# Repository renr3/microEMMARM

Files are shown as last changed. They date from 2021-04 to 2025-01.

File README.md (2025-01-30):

# microEMMARM
This is the official repository of the microEMMARM system. 

This repository was built and will be maintaned to provide all the necessary resources to deploy the open-source microEMMARM test system and perform an EMM-ARM test with it. This repository will constantly be updated for bug fixes, new versions and other updates/fixes. **Keep an eye on it!**

The microEMMARM project is released under MIT license. If you want to use for commercial ends, please check the restrictions imposed by the licenses that bind this work (both microEMMARM and the libraries that it uses). 

Punctual static releases made available in Zenodo will also be archived here.

If you are  interested in more details, explanation and results concerning the microEMMARM system, please check the papers below. Also, if you use this repository in some way, please consider citing a research paper that reports on this work:

1. **Rocha Ribeiro, R., Russo, T., Araghi, A., Granja, J. L., Azenha, M., & Lameiras, R. (2025). Design and validation of a minimalist, open-source system for measuring elastic modulus evolution in cementitious materials. Nondestructive Testing and Evaluation, 1–25.** 
2. Rocha Ribeiro, R., Sousa, M.I.C., Rêgo, J.H.d. Lameiras, R. Innovative low-cost system for early age E-modulus monitoring of cement pastes: validation and application to nanosilica-added and limestone-calcined clay cements. Mater Struct 55, 13 (2022). https://doi.org/10.1617/s11527-021-01849-w 
3. A cost-effective micro-controller based system for EMM-ARM tests in cement paste**: Rocha Ribeiro, R.; Granja, José; Lameiras, Rodrigo; Azenha, Miguel. (2022). Synercrete'23 conference. To be published.
4. R. Ribeiro and R. Lameiras, “Monitoring of elastic modulus evolution on concrete with a low-cost test system,” 2021, doi: https://doi.org/10.6084/m9.figshare.14773329.v1. 
5. R. Rocha Ribeiro, J. H. S. Rêgo, and R. Lameiras, “Elastic modulus evolution of cement pastes since early ages: development and application of a test system,” in Anais do 62o Congresso Brasileiro do Concreto - CBC2020, 2021, pp. 1–10, [Online]. Available: https://www.researchgate.net/publication/357605792_Elastic_modulus_evolution_of_cement_pastes_since_early_ages_development_and_application_of_a_test_system.

Any doubts, questions or messages may be directed to renan.rocha.ribeiro@gmail.com

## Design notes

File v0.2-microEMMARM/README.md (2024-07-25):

# microEMMARM v0.2

This is the official repository of microEMMARM v0.2, a microcontroller-based system for performing EMM-ARM (Elastic Modulus Measurement through Ambient Response Method) tests. Previous versions can be found in the other subrepos in this same repository (_i.e._, "V0.1.b-Synercrete23" and "v..1.a-Zenodo").

The information contained here are self-sufficient for allowing full reproduction of the data-acquisition hardware necessary for performing an EMM-ARM test. It includes the data-acquisition and storage hardware and the accelerometer sensors. As an output, this system will produce a series of ".emm" files, a binary-formatted file. To post-process these files and obtain the elastic modulus evolution, check the open-source post-processing software in https://github.com/renr3/postProcess-EMMARM.

For this version v0.2, the resources available are:

1. **cases**: files to support the production of hardcases for storing the system. There are two versions available: version 1, designed primarily for manufacturing with industrial plastic but that can also be manufactured with 3D printing; version 2, designed primarily to be produced in a small 3D printer, by printing small parts of the box and assemble it later with glue.
2. **documentation**: this folder is meant to contain information relevant to understanding design and working options for the system.
3. **libraries**: the necessary Arduino libraries for the source code of the hardware system
4. **pcb**: these are all the files necessary to build the PCB (printed circuit board) of the data-acquisition system. You can find: (i) the datasheets of each of the components used in the current implementation (so you may find the exact same ones or decide on substitutions); (ii) the gerber files in case you want to order the PCB from a manufacturer like https://jlcpcb.com/; (iii) an Excel spreadsheet with the bill of materials, containing the description, quantitiy, and estimated costs and links from three online suppliers; (iv) a Fritzing file with the schematics of the system to support building over a PCB, a solderable perfboard, or a PCB; (iv) a block diagram with the parts mapping, to aid in the navigation of the project files.
5. **source**: this is the Arduino source code that you would need to upload to the microcontroller. This version was designed for the ATMega328p microcontroller, but there should be no problem in using it with similar microcontrollers.

As mentioned in the root folder, the microEMMARM project is released under the MIT license, but please check the underlying licenses on the other libraries (check **libraries** folder) to see if your intended use is somewhat restricted.

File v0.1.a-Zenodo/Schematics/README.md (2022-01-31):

These schematics were developed in the Fritzing software (https://fritzing.org/).

Gerber files generated from the Fritzing software are also included.

For first time builders, it is recommended to follow the schematics in a solderless breadboard, or on a soldered perfboard, so a better understanding of the circuit is attained. For experienced users in electronics, the Gerber files may be used to directly print a PCB board.

The microEMMARM schematics currently have the following versions:

- beta_v0.0: this is the bare-minimum version, as shown in the Figure 3 of the research paper "Low-cost system for early age E-modulus monitoring of cement-based materials". This version does not have Gerber files. It is mainly intended for implementation on a solderless breadbor or a solderable breadbord (aka perfboard) for first time implementers.
- beta_v0.1: this is the bare-minimum version with added ADC channels and digital channels for controlling external devices through a digital interface (e.g. motors for artificial excitation). This version is still under testing and will be added in the near future. This version has Gerber files for PCB printing.

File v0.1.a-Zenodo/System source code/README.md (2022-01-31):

This folder contains the Arduino source code files required by the microprocessor to perform the automated tasks. 

In order to open the file and upload to the Arduino or to a properly bootloaded microprocessor, the user shall use the latest version of the Arduino IDE.

Installation of the libraries used by the source code may be required during uploading the source code.

The source code folders are named to indicate the respective hardware version they were built upon. Make sure you use the correct one, otherwise your system may not function well or may not function at all. In the end of the folders' name, the numeric code indicates the date that version was released, so to allow various source code versions for a given hardware design.

A brief summary of each version is presented here:

- **beta_v0.0-2104**: source code for beta_v0.0 hardware. Main features: single ADC channel; user interface comprised of 3 LEDs and a buttom; ADS1115 running on continuous mode with ALRT pin.

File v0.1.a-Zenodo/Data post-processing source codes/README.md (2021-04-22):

This folder contains the source codes of the software for EMM-ARM data post-processing and E-modulus estimation.

The source codes were developed in the MATLAB programming environment. Installation of the required toolboxes may be required.

The following 3 .m files were developed, and need to be subsequently manually run to perform all the post-processing tasks required during EMM-ARM data processing. 

Further improvements will aim towards building an integrated user interface for all these codes.

# 1 - Iterative frequency identification in all files (1_freqId file)

1. The code starts by asking the user to select the folder that contains all the test files.

2. The code iterates through each of the test files.

3. In each test file, the code automatically estimates the first "n" frequencies by using the peak-picking method.

4. In the beggining of the code, some configuration variables shall be set by the user: number of frequencies to be identified, digital filtering characteristics, etc.

5. The code generates a text file in which the time and frequency of each test file is printed in a space-separated file

# 2 - Iterative E-modulus estimation from the identified frequency in all files (2_EModEst file)

1. The code reads the result text file generated by the previous code and estimates the E-modulus from each natural frequency.

2. The code iterates through each line of the results text file and estimates the E-modulus.

3. In the beggining of the code, some configuration variables and input information are required: specimen length, mass at the tip, empty natural frequency of the mould and its length during the empty test for estimation of the mould's material E-modulus, etc.

4. The code generates a results text file in which the time and E-modulus associated to each test file is printed in a space-seprated file.

# 3 - E-modulus curve fitting in the identified E-modulus (3_EModCurveFit file)

1. The code fits a exponential evolution curve to the E-modulus results obtained from the results text file generated by the previous code.

2. The code generates a result file that contains the information about the fitted curve (value of the parameters and the R2 value) and the values of the fitted curve at each tested point, with the residuals at each point.

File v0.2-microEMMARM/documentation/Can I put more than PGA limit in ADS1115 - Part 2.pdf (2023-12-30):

LOCKED (https://forums.adafruit.com/posting.php?mode=reply&t=65300)

20 posts (https://forums.adafruit.com/viewtopic.php?t=65300) 1 (https://forums.adafruit.com/viewtopic.php?t=65300) 2

‹ Return to forum: Other Products from Adafruit (https://forums.adafruit.com/viewforum.php?f=19)

# ADS1115 may be destroyed

Moderators: adafruit_support_bill, (https://forums.adafruit.com/memberlist.php?mode=viewprofile&u=10091) adafruit (https://forums.adafruit.com/memberlist.php?mode=viewprofile&u=1096)

Please be positive and constructive with your questions and comments.

- Quick links

FORUMS INDEX (https://forums.adafruit.com/index.php) / SUPPORTED PRODUCTS & PROJECTS (https://forums.adafruit.com/viewforum.php?f=36)

Re: ADS1115 may be destroyed (https://forums.adafruit.com/viewtopic.php?p=366856#p366856)

jtomerli (https://forums.adafruit.com/memberlist.php?mode=viewprofile&u=285258)

- (https://forums.adafruit.com/viewtopic.php?p=366856#p366856) Mon Apr 20, 2015 9:30 am

Thanks loek, I will definitely check that if the problem crops up.

Re: ADS1115 may be destroyed (https://forums.adafruit.com/viewtopic.php?p=378481#p378481) jtomerli (https://forums.adafruit.com/memberlist.php?mode=viewprofile&u=285258)

- (https://forums.adafruit.com/viewtopic.php?p=378481#p378481) Mon Jun 01, 2015 2:26 pm
- loek wrote:
Hi jtomerli,

Nice that everything is now as you expected it!

If one day you should again have unstable outputs, put your DVM between the GND of the ADS1115 and any one of the 4 analog inputs. If you measure more than +5,3 V or less than -0,3 V,

Shop (https://www.adafruit.com/) Learn (https://learn.adafruit.com/) Blog (https://blog.adafruit.com/) | Forums (https://forums.adafruit.com/) | LIVE! (https://www.youtube.com/adafruit/live) AdaBox (https://www.adafruit.com/adabox) IO (https://io.adafruit.com/)

## - (https://www.adafruit.com/shopping_cart)

then that analog input is outside it's electrical range and you may be "frying" the ADS1115. I suspect your shunt was/is pushing it's 2 analog inputs to +18 V thus causing the erratic behaviour.

OK, so all was well for more than a month, now I am back to having an erratic reading. It fluctuates from -25 to +225 mV. Normal/expected is around 70 mV. 7A through a 10A/100mV shunt.

loek, I checked the voltage from the ground rail to the A0 & A2 pins of the ADS1115 and it was well within the Vcc range. A0/A1 are reading the shunt, A2/A3 are reading a nominal 4V signal (24V behind a 6:1 voltage divider).
I am posting my latest findings here: viewtopic.php?f=22&t=73330&p=378433#p378433 (https://forums.adafruit.com/viewtopic.php?f=22&t=73330&p=378433#p378433) Don't want to double post ( i put a schematic on a thread with the ADS1115 and reading shunts), but I wanted to update my last post. Thanks.

Re: ADS1115 may be destroyed (https://forums.adafruit.com/viewtopic.php?p=378631#p378631)

loek (https://forums.adafruit.com/memberlist.php?mode=viewprofile&u=290050)

- (https://forums.adafruit.com/viewtopic.php?p=378631#p378631) Tue Jun 02, 2015 2:06 am

Hi Jeff,

From your schematic I can't tell if the voltage-divider is just two resistors or if it also somehow connected to the Arduino? The fact that both PSU's might be "floating" could explain some erratic behaviour...

Not sure if you synchronise the analog measurements in any way with the PWM signal to the SSR? I assume you do and this code could be time critical and also lead to erratic results...

Loek.

Re: ADS1115 may be destroyed (https://forums.adafruit.com/viewtopic.php?p=378753#p378753)

jtomerli (https://forums.adafruit.com/memberlist.php?mode=viewprofile&u=285258)

- (https://forums.adafruit.com/viewtopic.php?p=378753#p378753) Tue Jun 02, 2015 12:54 pm

OK, preliminary fix, I used a voltage regulator running off of the 24VDC PSU to supply 9.8VDC to the Mega 2560, readings are rock steady.
My assumption is that tying the main PSU ground to the Arduino through the V reg fixed the issue of the fluctuating DC shunt readings.

LOCKED (https://forums.adafruit.com/posting.php?mode=reply&t=65300)

20 posts (https://forums.adafruit.com/viewtopic.php?t=65300) 1 (https://forums.adafruit.com/viewtopic.php?t=65300) 2

- Return to “Other Products from Adafruit” (https://forums.adafruit.com/viewforum.php?f=19)

Please be positive and constructive with your questions and comments.

Contact Us (https://adafruit.com/contact_us)
Tech Support Forums (https://forums.adafruit.com/)
FAQs (https://adafruit.com/faq)
Shipping & Returns (https://adafruit.com/shipping)
Terms of Service (https://adafruit.com/terms_of_service)
Privacy & Legal (https://adafruit.com/privacy)
Website Accessibility (https://adafruit.com/accessibility)

About Us (https://adafruit.com/about)
Press (https://adafruit.com/press)
Educators (https://adafruit.com/educators)
Distributors (https://adafruit.com/distributors)
Jobs (https://jobs.adafruit.com/)
Gift Cards (https://adafruit.com/category/14)

Re: ADS1115 may be destroyed (https://forums.adafruit.com/viewtopic.php?p=378815#p378815)

loek (https://forums.adafruit.com/memberlist.php?mode=viewprofile&u=290050)

- (https://forums.adafruit.com/viewtopic.php?p=378815#p378815) Tue Jun 02, 2015 4:29 pm

Yes, as long as the GND of the 24V PSU (left side of the shunt) is connected to the GND of the Arduino and hence to the GND of the AD1115, you should be OK. If not, the PSU's float and any resulting potential difference is effectively also between the analog inputs and GND of the AD1115, exactly where you do not want any overvoltage!

Hope all stays stable now.

Loek.

Jump to

FORUMS INDEX (https://forums.adafruit.com/index.php) | All times are UTC-04:00

- (https://www.instagram.com/adafruit/) (https://twitter.com/adafruit/) (https://www.facebook.com/adafruitindustries) (https://www.youtube.com/adafruit) (https://github.com/adafruit)

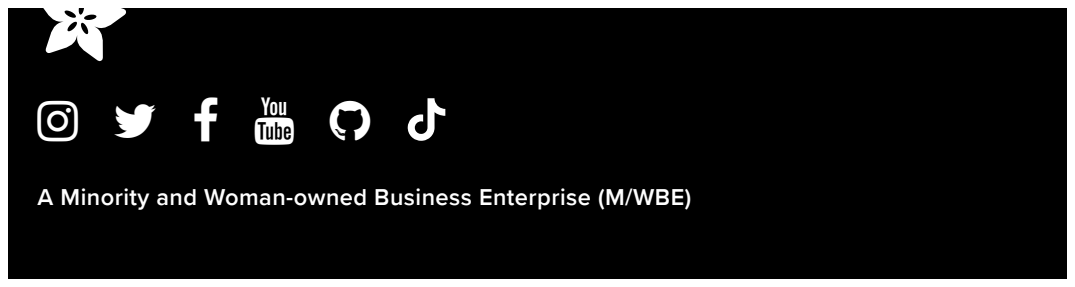
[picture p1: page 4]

A Minority and Woman-owned Business Enterprise (M/WBE) (https://adafruit.com/about)

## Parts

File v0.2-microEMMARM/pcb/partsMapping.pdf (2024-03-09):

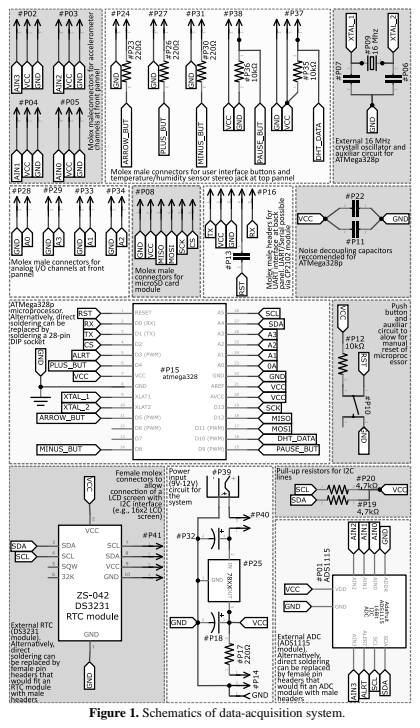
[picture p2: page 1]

Figure 1. Schematics of data-acquisition system.

2

Table 1. Electronic components of the data-acquisition system.
Id. | Description | Purpose/location
Printed board circuit components and modules
P11, P13, P22 | 0.1μF electrolytic capacitor | Noise decoupling at power and serial lines
P18, P32 | 10 μF electrolytic capacitor | Noise filter
P12, P35, P36 | 10kΩ resistor | Pull-up or -down resistors
P09 | 16MHz crystal | 16MHz external crystal oscillator
P15 | 28-pin socket | 28-pin socket for the ATmega328p
P17, P23, P26,
P30 | 220Ω resistor | Resistors to control current drainage
P06, P07 | 22pF ceramic capacitor | 22pf ceramic capacitor for atmega328p
P19, P20 | 4.7kΩ resistor | Pull-up resistors for I2C lines
P01 | ADS1115 module | Direct soldering the module can be substituted
| | by 10 female pin headers for ADS1115
P39 | DC input jack | Power input for a 9V-12V AC-DC voltage
P21a, P21b | DS3231 module | Direct soldering the module can be substituted
| | by 6 female pin headers for DS3231
P25 | LM7805 | Voltage regulator
P14, P24,
P27-29, P31, P33-34, P38, P40 | Molex with 2 pins¹ | Connectors for various panel buttons and con-
| | nectors
P37, P02-05 | Molex with 3 pins¹ | Connection for temperature and humidity sen-
| | sor and accelerometer channels
P41 | Molex with 4 pins¹ | Connection for LCD screen module²
P16 | Molex with 5 pins¹ | CP2102 connector for USB/UART communi-
| | cation with ATmega328p
P08 | Molex with 6 pins¹ | Connection for microSD module²
P08b | microSD module | MicroSD module with SPI connectors
P10 | PCB push button | Push button to allow atmega328p hard reset
Buttons, connectors, and modules to install in external case
P42-45 | (On)-Off panel button | Momentary pushbutton, normally open and
| | 12mm mounting hole diameter, at top panel
P46, P51-54 | 3.5 mm jack PJ-301M | Stereo audio panel connector with 3 pins for
| | temperature and humidity sensor at top panel
| | and analog input/output at front panel
P47-50 | 3 way panel connector | Connectors for accelerometer at front panel
P55 | 5 way panel connector | Connector for a CP2102 module to enable se-
| | rial communication at back panel
P56 | On-Off panel button | Self-lock button, 12mm mounting hole diame-
| | ter, at back panel
P57 | LED + Panel LED holder | LED to indicate system is powered up
P58 | LCD screen module | 16x2 LCD screen module with I2C interface
P59 | microSD card module | MicroSD card module with SPI interface
Notes:
1 –Molex connectors comprise the header, the wire-board receptacle, and crimp terminals. 2 – The LCD screen and microSD card modules are not directly soldered on the PCB. Therefore, an extra pair of connectors are needed to connect the PCB to the modules.

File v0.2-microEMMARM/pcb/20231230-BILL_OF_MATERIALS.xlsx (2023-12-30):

Quantity | Description | Reference document (see datasheet folder) | Quotations per unit |  |  |  |  |  |  |  |  |  |  |  |  | Average total price
 |  |  | Price 1 |  |  |  | Price 2 |  |  |  | Price 13 |  |  |  | Average unit price
 |  |  | Unit price | Manufacter Part. No. | Retail | Link | Unit price | Manufacter Part. No. | Retail | Link | Unit price | Manufacter Part. No. | Retail | Link
3 | 0.1uF electrolytic capacitor | 1 | 0.064 | MCRH100V104M5X11 | Farnell | https://pt.farnell.com/multicomp/mcrh100v104m5x11/cap-0-1-f-100v-20/dp/1902938 | 0.228 | MCRH100V104M5X11 | Newark | https://www.newark.com/multicomp/mcrh100v104m5x11/aluminium-electrolytic-capacitor/dp/55T0578 | 0.034 | MCRH100V104M5X11 | element14 | https://sg.element14.com/multicomp/mcrh100v104m5x11/cap-0-1-f-100v-20/dp/1902938 | 0.1086666667 | 0.326
2 | 10 uF electrolytic capacitor | 2 | 0.157 | ECA1EAK100X | Farnell | https://pt.farnell.com/panasonic/eca1eak100x/cap-10-f-25v-20/dp/8766754 | 0.254 | ECA1EAK100X | Newark | https://www.newark.com/panasonic/eca1eak100x/aluminum-electrolytic-capacitor/dp/38K1156 | 0.258 | ECA1EAK100X | element14 | https://sg.element14.com/panasonic/eca1eak100x/cap-10-f-25v-20/dp/8766754 | 0.223 | 0.446
3 | 10kΩ resistor | 3 | 0.0578 | MCCFR0W8J0103A20 | Farnell | https://pt.farnell.com/multicomp-pro/mccfr0w8j0103a20/carbon-film-resistor-10kohm-125mw/dp/1128067?st=10%20k%20resistor | 0.006 | MCCFR0W8J0103A20 | Newark | https://www.newark.com/multicomp-pro/mccfr0w8j0103a20/carbon-film-resistor-10kohm-125mw/dp/58K5083 | 0.009 | 1-2199298-9 | element14 | https://sg.element14.com/multicomp-pro/mccfr0w8j0103a20/carbon-film-resistor-10kohm-125mw/dp/1128067 | 0.02426666667 | 0.0728
1 | 16MHz crystal | 4 | 0.476 | A-16.000-18 | Farnell | https://pt.farnell.com/raltron/a-16-000-18/crystal-16mhz-18pf-hc-49u/dp/1385933?st=16%20mhz%20crystal | 0.426 | A-16.000-18 | Newark | https://www.newark.com/raltron/a-16-000-18/crystal-16mhz-18pf-hc-49u/dp/18M8537 | 0.428 | A-16.000-18 | element14 | https://sg.element14.com/raltron/a-16-000-18/crystal-16mhz-18pf-hc-49u/dp/1385933 | 0.4433333333 | 0.4433333333
1 | 28-pin microprocessor socket | 5 | 0.597 | 1-2199298-9 | Farnell | https://pt.farnell.com/te-connectivity/1-2199298-9/ic-socket-dip-28pos-th/dp/2445626?st=28%20pin%20socket | 0.89 | 1-2199298-9 | Digikey | https://www.digikey.pt/en/products/detail/1-2199298-9/A120353-ND/5022045 | 0.696 | 1-2199298-9 | TE connectivity | https://www.te.com/usa-en/product-1-2199298-9.html?te_bu=Cor&te_type=srch&elqCampaignId=147303 | 0.7276666667 | 0.7276666667
1 | ATMega328p | 29 | 3.39 | ATMEGA328P-PU | Farnell | https://pt.farnell.com/microchip/atmega328p-pu/mcu-8bit-atmega-20mhz-dip-28/dp/1715487?st=atmega328p | 2.8 | ATMEGA328P-PU | TME | https://www.tme.eu/en/details/atmega328p-pu/8-bit-avr-family/microchip-atmel | 2.61 | ATMEGA328P-PU | Microchip | https://www.microchipdirect.com/product/ATMEGA328P-PU?productLoaded=true | 2.933333333 | 2.933333333
4 | 220Ω resistor | 6 | 0.012 | CFR25J220R | Farnell | https://pt.farnell.com/te-connectivity/cfr25j220r/res-220r-5-330mw-axial-carbon/dp/2329643?st=220%20resistor | 0.039 | CFR25J220R | TE Store | https://www.te.com/usa-en/product-5-1623930-4.html | 0.1 | CFR25J220R | Digikey | https://www.digikey.pt/en/products/detail/CFR25J220R/A141517CT-ND/9648730 | 0.05033333333 | 0.2013333333
2 | 22pf ceramic capacitor | 7 | 0.306 | S220K25SL0N63L6R | Farnell | https://pt.farnell.com/vishay/s220k25sl0n63l6r/cap-22pf-1-kv-10-sl/dp/2860152 | 0.46 | S220K25SL0N63L6R | Mouser | https://pt.mouser.com/ProductDetail/Vishay-BC-Components/S220K25SL0N63L6R | 0.41 | S220K25SL0N63L6R | Digikey | https://www.digikey.pt/en/products/detail/S220K25SL0N63L6R/1270PH-ND/2356806 | 0.392 | 0.784
2 | 4.7kΩ resistor | 8 | 0.014 | LR0204F4K7 | Farnell | https://pt.farnell.com/te-connectivity/lr0204f4k7/res-4k7-1-250mw-axial-metal-film/dp/2329947 | 0.05802 | LR0204F4K7 | TE Store | https://www.te.com/usa-en/product-1622247-1.html | 0.043 | LR0204F4K7 | Avnet | https://www.avnet.com/shop/us/products/te-connectivity/lr0204f4k7-3074457345645031254 | 0.03834 | 0.07668
1 | DC input jack | 9 | 0.599 | DCJ200-10-A-K1-K | Farnell | https://www.avnet.com/shop/us/products/te-connectivity/lr0204f4k7-3074457345645031254?CMP=EMA_Octopart_inventoryfeed_VSE | 0.863 | DCJ200-10-A-K1-K | Newark | https://www.newark.com/gct-global-connector-technology/dcj200-10-a-k1-k/dc-power-jack-5a-20vdc-black/dp/75Y6644 | 0.639 | DCJ200-10-A-K1-K | element14 | https://sg.element14.com/gct-global-connector-technology/dcj200-10-a-k1-k/dc-power-jack-5a-20vdc-black/dp/2673246 | 0.7003333333 | 0.7003333333
1 | LM7805 | 10 | 0.957 | MC7805ACTG | Farnell | https://pt.farnell.com/on-semiconductor/mc7805actg/ic-v-reg-5-0v-7805-to-220-3/dp/9664505?ost=lm7805&iscrfnonsku=true | 0.86 | MC7805ACTG | Digikey | https://www.digikey.pt/en/products/detail/MC7805ACTG/MC7805ACTGOS-ND/1481210 | 0.87 | MC7805ACTG | Mouser | https://pt.mouser.com/ProductDetail/onsemi/MC7805ACTG?qs=%252B9%2Fcbd0IE0S3%2FunkJ%2FONRg%3D%3D | 0.8956666667 | 0.8956666667
12 | Molex 2 pins 180° header | 11 | 0.22 | 22-23-2021 | Farnell | https://pt.farnell.com/molex/22-23-2021/connector-header-2pos-1row-2-54mm/dp/1462926?MER=TARG-MER-PDP-RECO-STM71168 | 0.18 | 22-23-2021 | Mouser | https://pt.mouser.com/ProductDetail/Molex/22-23-2021?qs=ILqg114nvd4YKlRlbo3yMg%3D%3D | 0.21 | 22-23-2021 | Digikey | https://www.digikey.pt/en/products/detail/0022232021/900-0022232021-ND/26667 | 0.2033333333 | 2.44
12 | Molex 2 pins 180° receptacle | 15 | 0.16 | 22-01-3027 | Farnell | https://pt.farnell.com/molex/22-01-3027/connector-rcpt-2pos-1row-2-54mm/dp/1462825 | 0.158 | 22-01-3027 | Avnet | https://www.avnet.com/shop/us/products/molex/22-01-3027-3074457345643196670 | 0.22 | 22-01-3027 | Mouser | https://pt.mouser.com/ProductDetail/Molex/22-01-3027?qs=cRUT3GdJqnwywyFd19%252BSsA%3D%3D | 0.1793333333 | 2.152
5 | Molex 3 pins 180° header | 12 | 0.28 | 22-23-2031 | Farnell | https://pt.farnell.com/molex/22-23-2031/connector-header-3pos-1row-2-54mm/dp/1462950?MER=sy-me-pd-mi-alte | 0.27 | 22-23-2031 | Digikey | https://www.digikey.pt/en/products/detail/0022232031/WM4201-ND/26669 | 0.128 | 22-23-2031 | Avnet | https://www.avnet.com/shop/us/products/molex/22-23-2031-3074457345626470039 | 0.226 | 1.13
5 | Molex 3 pins 180° receptacle | 16 | 0.17 | 22-01-2037 | Farnell | https://pt.farnell.com/molex/22-01-2037/connector-rcpt-3pos-1row-2-54mm/dp/1462834 | 0.16 | 22-01-2037 | Digikey | https://www.digikey.pt/en/products/detail/0022012037/WM2012-ND/171992 | 0.191 | 2037-01-22 | Avnet | https://www.avnet.com/shop/us/products/molex/22-01-2037-3074457345643196726 | 0.1736666667 | 0.8683333333
2 | Molex 4 pins 180° header | 13 | 0.58 | 22-23-2041 | Farnell | https://pt.farnell.com/molex/22-23-2041/connector-header-4pos-1row-2-54mm/dp/1462920?MER=TARG-MER-PDP-RECO-STM71168 | 0.33 | 22-23-2041 | Mouser | https://pt.mouser.com/ProductDetail/Molex/22-23-2041?qs=ILqg114nvd5W6e%252BaZws1Xg%3D%3D | 0.36 | 22-23-2041 | Digikey | https://www.digikey.pt/en/products/detail/0022232041/WM4202-ND/26671 | 0.4233333333 | 0.8466666667
2 | Molex 4 pins 180° receptacle | 17 | 0.23 | 22-01-2047 | Farnell | https://pt.farnell.com/molex/22-01-2047/connector-rcpt-4pos-1row-2-54mm/dp/1462809 | 0.05421 | 22-01-2047 | Heilind | https://estore.heilind.de/?page=item-search-results&query=22-01-2047 | 0.097 | 22-01-2047 | Avnet | https://www.avnet.com/shop/us/products/molex/22-01-2047-3074457345626398365 | 0.12707 | 0.25414
1 | Molex 5 pins 180° header | 14 | 0.45 | 22-23-2051 | Farnell | https://pt.farnell.com/molex/22-23-2051/connector-header-5pos-1row-2-54mm/dp/1462952 | 0.42 | 22-23-2051 | Digikey | https://www.digikey.pt/en/products/detail/0022232051/WM4203-ND/26673 | 0.41 | 22-23-2051 | Mouser | https://pt.mouser.com/ProductDetail/Molex/22-23-2051?qs=ILqg114nvd59B%2FNFe4wunQ%3D%3D | 0.4266666667 | 0.4266666667
1 | Molex 5 pins 180° receptacle | 18 | 0.29 | 22-01-3057 | Farnell | https://pt.farnell.com/molex/22-01-3057/connector-rcpt-5pos-1row-2-54mm/dp/1462874 | 0.18 | 22-01-3057 | Mouser | https://pt.mouser.com/ProductDetail/Molex/22-01-3057?qs=dvxwXVM4mZX5H9Q4idh0EQ%3D%3D | 0.06983 | 22-01-3057 | Heilind | https://estore.heilind.de/?page=item-search-results&query=22-01-3057 | 0.1799433333 | 0.1799433333
2 | Molex 6 pins 180° header | 34 | 0.69 | 22-23-2061 | Farnell | https://pt.farnell.com/molex/22-23-2061/connector-header-6pos-1row-2-54mm/dp/1462922 | 0.46 | 22-23-2061 | Digikey | https://www.digikey.pt/en/products/detail/0022232061/WM4204-ND/26675 | 0.268 | 22-23-2061 | Distrelec | https://www.distrelec.biz/en/kk-254-through-hole-pcb-straight-contacts-rows-54mm-pitch-molex-22-23-2061/p/30065097 | 0.4726666667 | 0.9453333333
2 | Molex 6 pins 180° receptacle | 19 | 0.44 | 22-01-3067 | Farnell | https://pt.farnell.com/molex/22-01-3067/connector-rcpt-6pos-1row-2-54mm/dp/1654529 | 0.47 | 22-01-3067 | Digikey | https://www.digikey.pt/en/products/detail/0022013067/WM2004-ND/26439 | 0.46 | 22-01-3067 | Mouser | https://pt.mouser.com/ProductDetail/Molex/22-01-3067?qs=cRUT3GdJqnx%252BQBgba2oxqQ%3D%3D | 0.4566666667 | 0.9133333333
64 | KK crimp terminals | 20 | 0.0916 | 08-51-0108 | Farnell | https://pt.farnell.com/molex/08-51-0108/contact-socket-30-22awg-crimp/dp/3103147?st=kk%202759 | 0.056 | 08-51-0108 | Newark | https://www.newark.com/molex/08-51-0108/contact-socket-30-22awg-crimp/dp/03AH3780 | 0.1 | 08-51-0108 | Digikey | https://www.digikey.pt/en/products/detail/0008510108/WM19393CT-ND/8638483 | 0.08253333333 | 5.282133333
1 | PCB push button | 33 | 0.138 | PHAP5-30VA2B3T2N2 | Farnell | https://pt.farnell.com/apem/phap5-30va2b3t2n2/tactile-switch-0-05a-12vdc-260gf/dp/3796573?st=push%20button%20pcb%20tht | 0.1428 | PHAP5-30VA2B3T2N2 | Distrelec | https://www.distrelec.biz/en/tactile-switch-phap5-30-no-6n-6mm-apem-phap5-30va2b3t2n2/p/30251924 | 0.103 | PHAP5-30VA2B3T2N2 | TTI Europe | https://www.ttieurope.com/content/ttieurope/en/apps/part-detail.html | 0.1279333333 | 0.1279333333
4 | Momentary (On)-Off panel pushbutton | 21 | 1.03 | MCPS25B-3 | Farnell | https://pt.farnell.com/multicomp/mcps25b-3/pushbutton-switch-spst-1a-250v/dp/2913862 | 1.43 | MCPS25B-3 | Newark | https://www.newark.com/multicomp-pro/mcps25b-3/pushbutton-switch-spst-1a-250v/dp/69AC6100 | 1.213 | MCPS25B-3 | element14 | https://sg.element14.com/multicomp/mcps25b-3/pushbutton-switch-spst-1a-250v/dp/2913862 | 1.224333333 | 4.897333333
1 | Self-locking On-Off panel pushbutton | 22 | 1.03 | MCPS25A-3 | Farnell | https://pt.farnell.com/multicomp/mcps25a-3/pushbutton-switch-spst-1a-250v/dp/2913866?ost=mcps25a-3 | 1.43 | MCPS25A-3 | Newark | https://www.newark.com/multicomp-pro/mcps25a-3/pushbutton-switch-spst-1a-250v/dp/69AC6096 | 1.213 | MCPS25A-3 | element14 | https://sg.element14.com/multicomp/mcps25a-3/pushbutton-switch-spst-1a-250v/dp/2913866 | 1.224333333 | 1.224333333
0 | Audio jack for panel, 3 contacts, 3.5 mm | 23 | 0.771 | MJ-355W | Farnell | https://pt.farnell.com/multicomp-pro/mj-355w/socket-3-5mm-jack-pk5/dp/1267384?st=PANEL | 4.55 | MJ-355W | Newark | https://www.newark.com/pro-signal/mj-355w/connector-rca-phono-jack-3-position/dp/26M1581 | 1.71 | MJ-355W | Distrelec | https://www.distrelec.biz/en/jack-panel-socket-vertical-mm-poles-marushin-electric-mj-355w/p/14270112 | 2.343666667 | 0
1 | Circular connector, panel mount, at least 3 ways | 24 | 1.58 | PSG01593 | Farnell | https://pt.farnell.com/pro-signal/psg01593/plug-multipole-panel-4way/dp/1280759?st=circular%20panel%20connector | 1.838 | PSG01593 | Newark | https://www.newark.com/pro-signal/psg01593/product-range/dp/24M6405 | 1.093 | PSG01593 | element14 | https://sg.element14.com/pro-signal/psg01593/plug-multipole-panel-4way/dp/1280759 | 1.503666667 | 1.503666667
1 | Circular connector, cable mount, at least 3 ways | 25 | 1.58 | PSG01590 | Farnell | https://pt.farnell.com/pro-signal/psg01590/circular-connector-receptacle/dp/1280756?MER=sy-me-pd-mi-acce | 1.095 | PSG01590 | element14 | https://sg.element14.com/pro-signal/psg01590/circular-connector-receptacle/dp/1280756 | 1.841 | PSG01590 | Newark | https://www.newark.com/pro-signal/psg01590/product-range/dp/26M2076 | 1.505333333 | 1.505333333
0 | Circular connector, panel mount, at least 5 ways | 26 | 1.06 | PSG01594 | Farnell | https://pt.farnell.com/pro-signal/psg01594/plug-multipole-5way/dp/1280760?st=circular%20panel%20connector | 0.702 | PSG01594 | element14 | https://sg.element14.com/pro-signal/psg01594/plug-multipole-5way/dp/1280760 | 1.128 | PSG01594 | Newark | https://www.newark.com/pro-signal/psg01594/circular-connector-plug-5-pin/dp/24M6406 | 0.9633333333 | 0
1 | LED 5mm | 27 | 0.166 | C503B-RAN-CZ0C0AA1 | Farnell | https://pt.farnell.com/cree/c503b-ran-cz0c0aa1/led-5mm-red-32-9cd-624nm/dp/2840473?st=led%20red%205mm | 0.15 | C503B-RAN-CZ0C0AA1 | Digikey | https://www.digikey.pt/en/products/detail/C503B-RAN-CZ0C0AA1/C503B-RAN-CZ0C0AA1-ND/6561758 | 0.15 | C503B-RAN-CZ0C0AA1 | Mouser | https://pt.mouser.com/ProductDetail/Cree-LED/C503B-RAN-CZ0C0AA1 | 0.1553333333 | 0.1553333333
1 | Panel LED holder, 5mm | 28 | 0.63 | CLP127BLK | Farnell | https://pt.farnell.com/vcc-visual-communications-company/clp127blk/led-mounting-clip/dp/2293486 | 0.62 | CLP127BLK | Digikey | https://www.digikey.pt/en/products/detail/CLP_127_BLK/CLP_127_BLK-ND/4515445 | 0.57 | CLP127BLK | Mouser (https://eu.mouser.com/ProductDetail/VCC/CLP_127_BLK) | https://eu.mouser.com/ProductDetail/VCC/CLP_127_BLK | 0.6066666667 | 0.6066666667
1 | ADS1115 module | 30 | 15.16 | ADAFRUIT 1085 | Digikey | https://www.digikey.pt/pt/products/detail/adafruit-industries-llc/1085/5761229 | 9.5 | JOY-IT KY-053 | Mauser | https://mauser.pt/catalog/product_info.php?cPath=1667_2604_2204&products_id=096-7616 | 15.73 | ADAFRUIT 1085 | Distrelec | https://www.distrelec.biz/en/ads1115-16-bit-adc-board-adafruit-1085/p/30091131?ext_cid=ceoctaqzzen-na | 13.46333333 | 13.46333333
1 | DS3231 module | 31 | 8.2 | DS3231+AT24C32 module | Mauser | https://mauser.pt/catalog/product_info.php?products_id=096-8833 | 5.6 | ARD01039 | bot'n'roll | https://www.botnroll.com/pt/arduino-acessorios/1614-modulo-rtc-ds3231.html | 7.82 | EF16B0024BG | Electrofun | https://www.electrofun.pt/comunicacao/modulo-rtc-ds3231-relogio | 7.206666667 | 7.206666667
1 | microSD card module | 32 | 4.49 | PTR006540 | PTRobotics | https://www.ptrobotics.com/conversores/6540-microsd-card-adapter-w-level-shifters.html | 2.95 | ARD01051 | bot'n'roll | https://www.botnroll.com/pt/arduino-acessorios/4152-m-dulo-leitor-cart-es-micro-sd-interface-spi.html | 6.48 | DFR0229 | DFRobot | https://www.digikey.pt/pt/products/detail/dfrobot/DFR0229/6588460 | 4.64 | 4.64
1 | 16X2 LCD screen I2C module | 35 | 8.29 | EF16A0036OK | Electrofun | https://www.electrofun.pt/display/display-lcd-i2c | 7.9 | LCD01100 | bot'n'roll | https://www.botnroll.com/pt/lcds-e-displays/2989-display-i2c-lcd1602-16x2-c-driver-p-funduino-azul.html | 8.18 | PTR005097 | PTRobotics | https://www.ptrobotics.com/lcd-alfanumerico/5097-16x2-i2c-lcd-module.html | 8.123333333 | 8.123333333
1 | ADXL 335 breakout board | 36a, 36b | 14.7 | PTR004892 | PTRobotics | https://www.ptrobotics.com/acelerometros/4892-gy-61-adxl335-triple-axis-accelerometer-module.html | 12.02 | EF18B0289BG | Electrofun | https://www.electrofun.pt/sensores-arduino/modulo-acelerometro-3-eixos-adxl335 | 18.35 | SEN01002 | bot'n'roll | https://www.botnroll.com/pt/acelerometros/228-sen-09269-acelerometro-de-3-eixos-analogico.html | 15.02333333 | 15.02333333
0 | DHT 22 module | 37 | 10.95 | PTR002332 | PTRobotics | https://www.ptrobotics.com/atmosfericos/2332-dht22-temperature-humidity-sensor.html | 9.4 | EF16A0052OK | Electrofun | https://www.electrofun.pt/sensores-arduino/sensor-humidade-temperatura-dht22 | 11.6 | SEN06002 | bot'n'roll | https://www.botnroll.com/pt/temperatura/325-sensor-de-temperatura-e-humidade-rht03.html | 10.65 | 0
5 | 24 AWG cables (meter) | 38 | 1.71 | PP002606 | Farnell | https://pt.farnell.com/pro-power/pp002606/ribbon-cable-6cond-24awg-per-m/dp/3050572?st=24%20awg | 1.932 | PP002606 | element14 | https://sg.element14.com/pro-power/pp002606/ribbon-cable-6cond-24awg-per-m/dp/3050572 | 1.2 | CAB01054 | bot'n'roll | https://www.botnroll.com/pt/multicondutores/2743-flat-cable-colorido-1-27mm-14x28awg-1metro.html | 1.614 | 8.07
1 | PCB wafer | See schematics | 23.11 | - | JLCPCB | https://jlcpcb.com/?_ga=2.233859930.596803965.1669117591-1780557897.1669117591 | 27.86894 | - | PCBWay | https://www.pcbway.com/ | 28.043 | - | PCBGoGo | https://www.pcbgogo.com/ | 26.34064667 | 26.34064667
1 | External box (3D printed) | See model | 1.61 |  | In-house printer |  |  |  |  |  | 0 |  |  |  | 0.805 | 0.805
 |  |  |  |  |  |  |  |  |  |  |  |  |  |  | Total: | €116.74
Values converted from dollars to euros with a rate 1 USD = 0.967 EUR

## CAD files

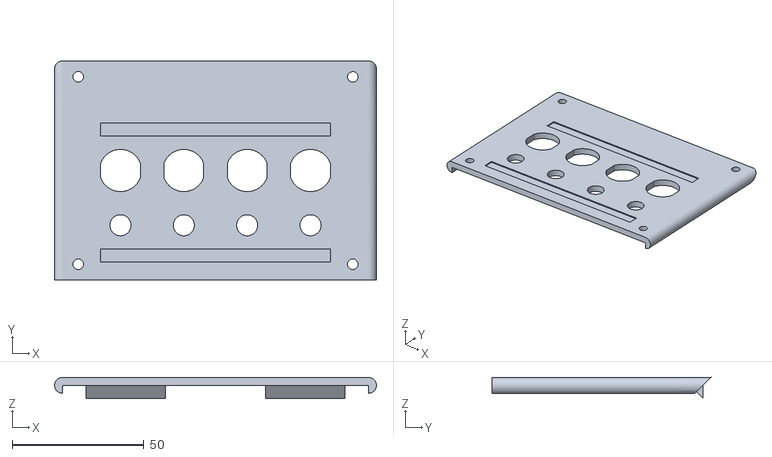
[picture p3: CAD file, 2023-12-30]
v0.2-microEMMARM/cases/version_2/0-FRONT_PANEL-toPrint v1.stl
122.0 x 83.0 x 8.00

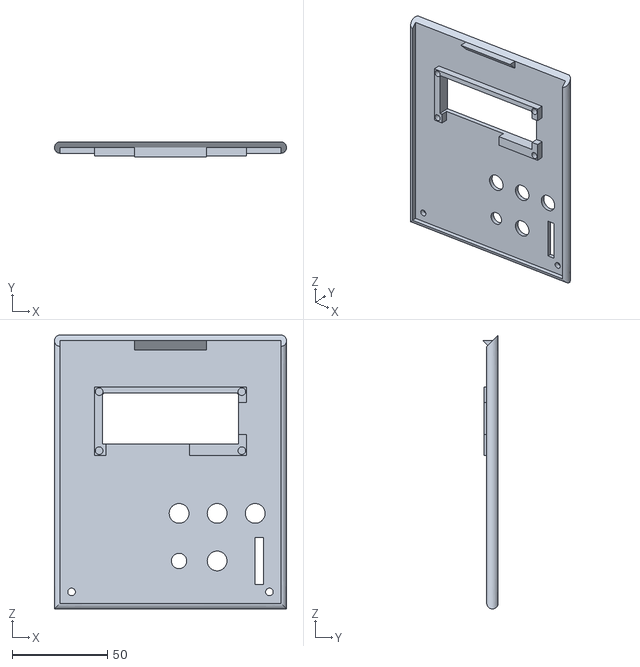
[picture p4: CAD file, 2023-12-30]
v0.2-microEMMARM/cases/version_2/0-TOP_PANEL-toPrint v1.stl
122.0 x 8.00 x 144.0

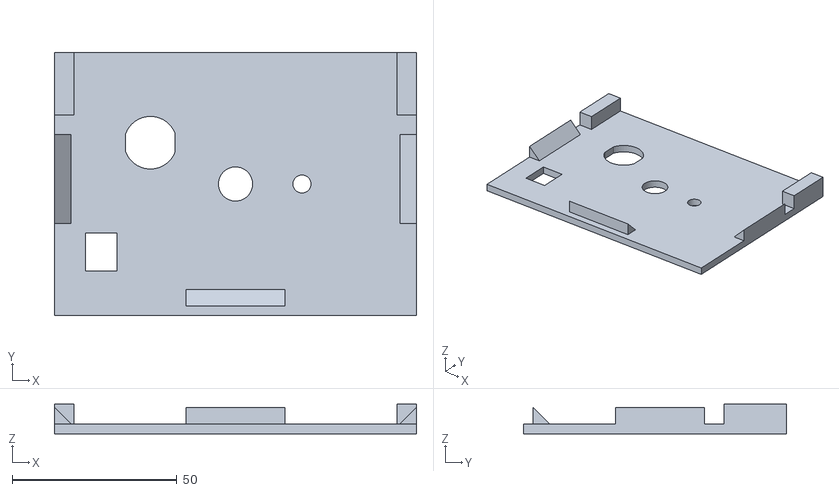
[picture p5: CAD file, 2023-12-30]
v0.2-microEMMARM/cases/version_2/0-BACK-PANEL-toPrint v1.stl
110.0 x 80.0 x 9.00

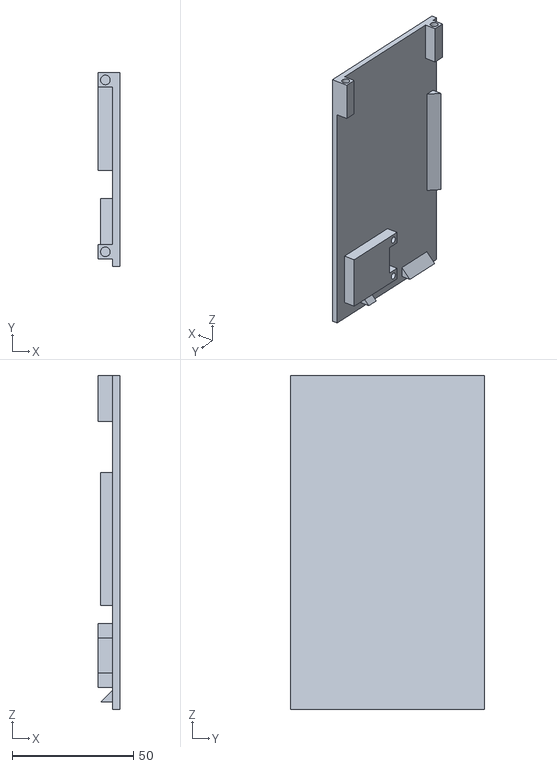
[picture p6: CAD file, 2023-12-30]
v0.2-microEMMARM/cases/version_2/0-SIDE-PANEL-2-toPrint v1.stl
9.00 x 80.0 x 138.0

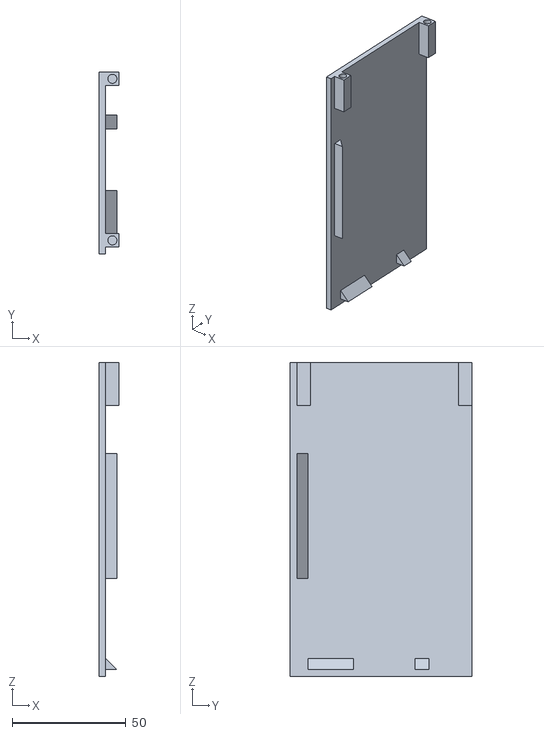
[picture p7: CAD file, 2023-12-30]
v0.2-microEMMARM/cases/version_2/0-SIDE-PANEL-1-toPrint v1.stl
9.00 x 80.0 x 138.0

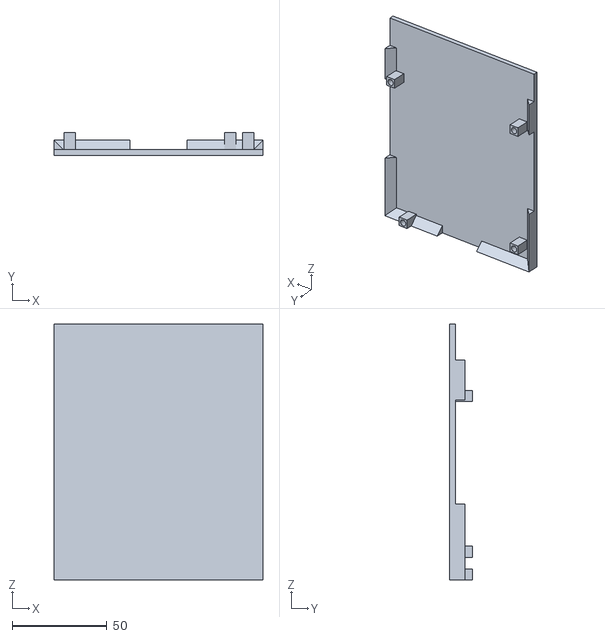
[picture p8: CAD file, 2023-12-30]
v0.2-microEMMARM/cases/version_2/0-BOTTOM-PANEL-toPrint v1.stl
110.0 x 12.0 x 135.0

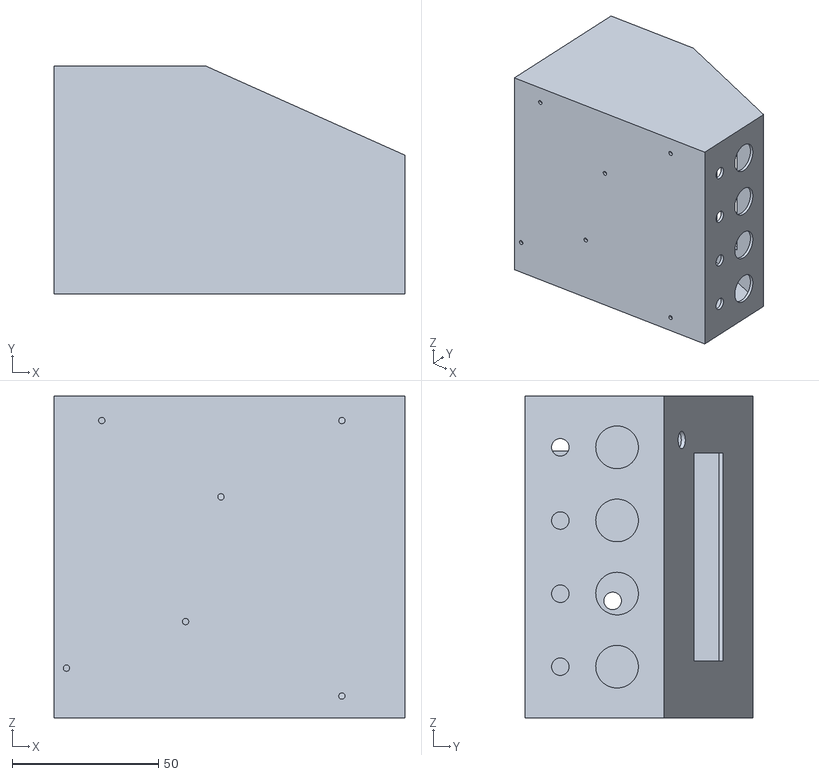
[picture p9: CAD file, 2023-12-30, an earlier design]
v0.2-microEMMARM/cases/version_1/Case_microEMMARM_20210619_v0.1 v14.stl
120.0 x 78.0 x 110.0

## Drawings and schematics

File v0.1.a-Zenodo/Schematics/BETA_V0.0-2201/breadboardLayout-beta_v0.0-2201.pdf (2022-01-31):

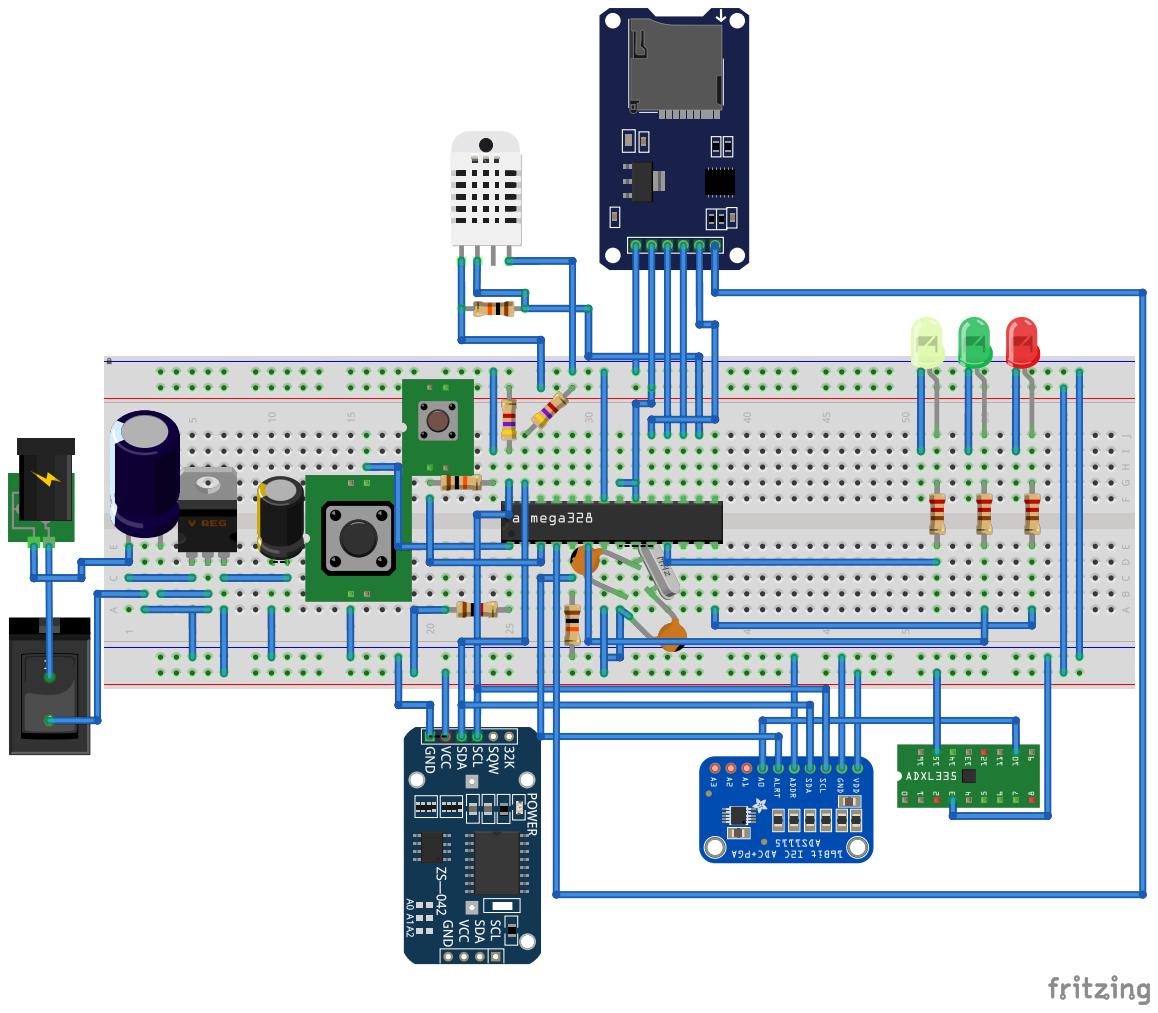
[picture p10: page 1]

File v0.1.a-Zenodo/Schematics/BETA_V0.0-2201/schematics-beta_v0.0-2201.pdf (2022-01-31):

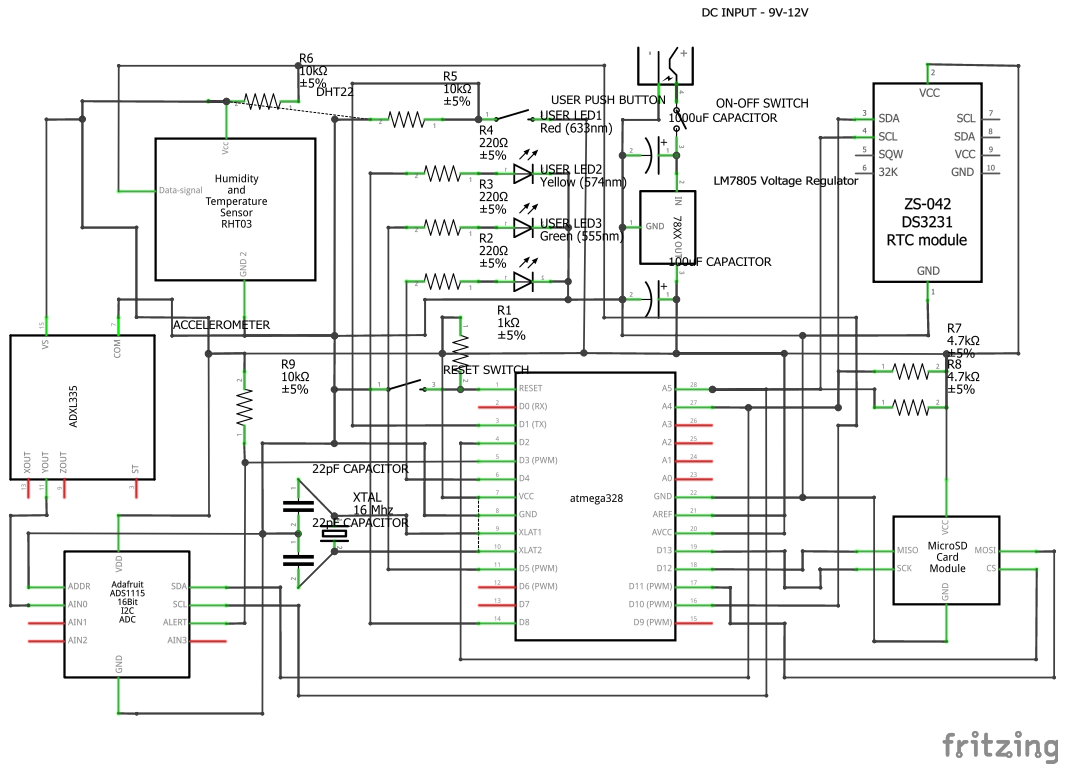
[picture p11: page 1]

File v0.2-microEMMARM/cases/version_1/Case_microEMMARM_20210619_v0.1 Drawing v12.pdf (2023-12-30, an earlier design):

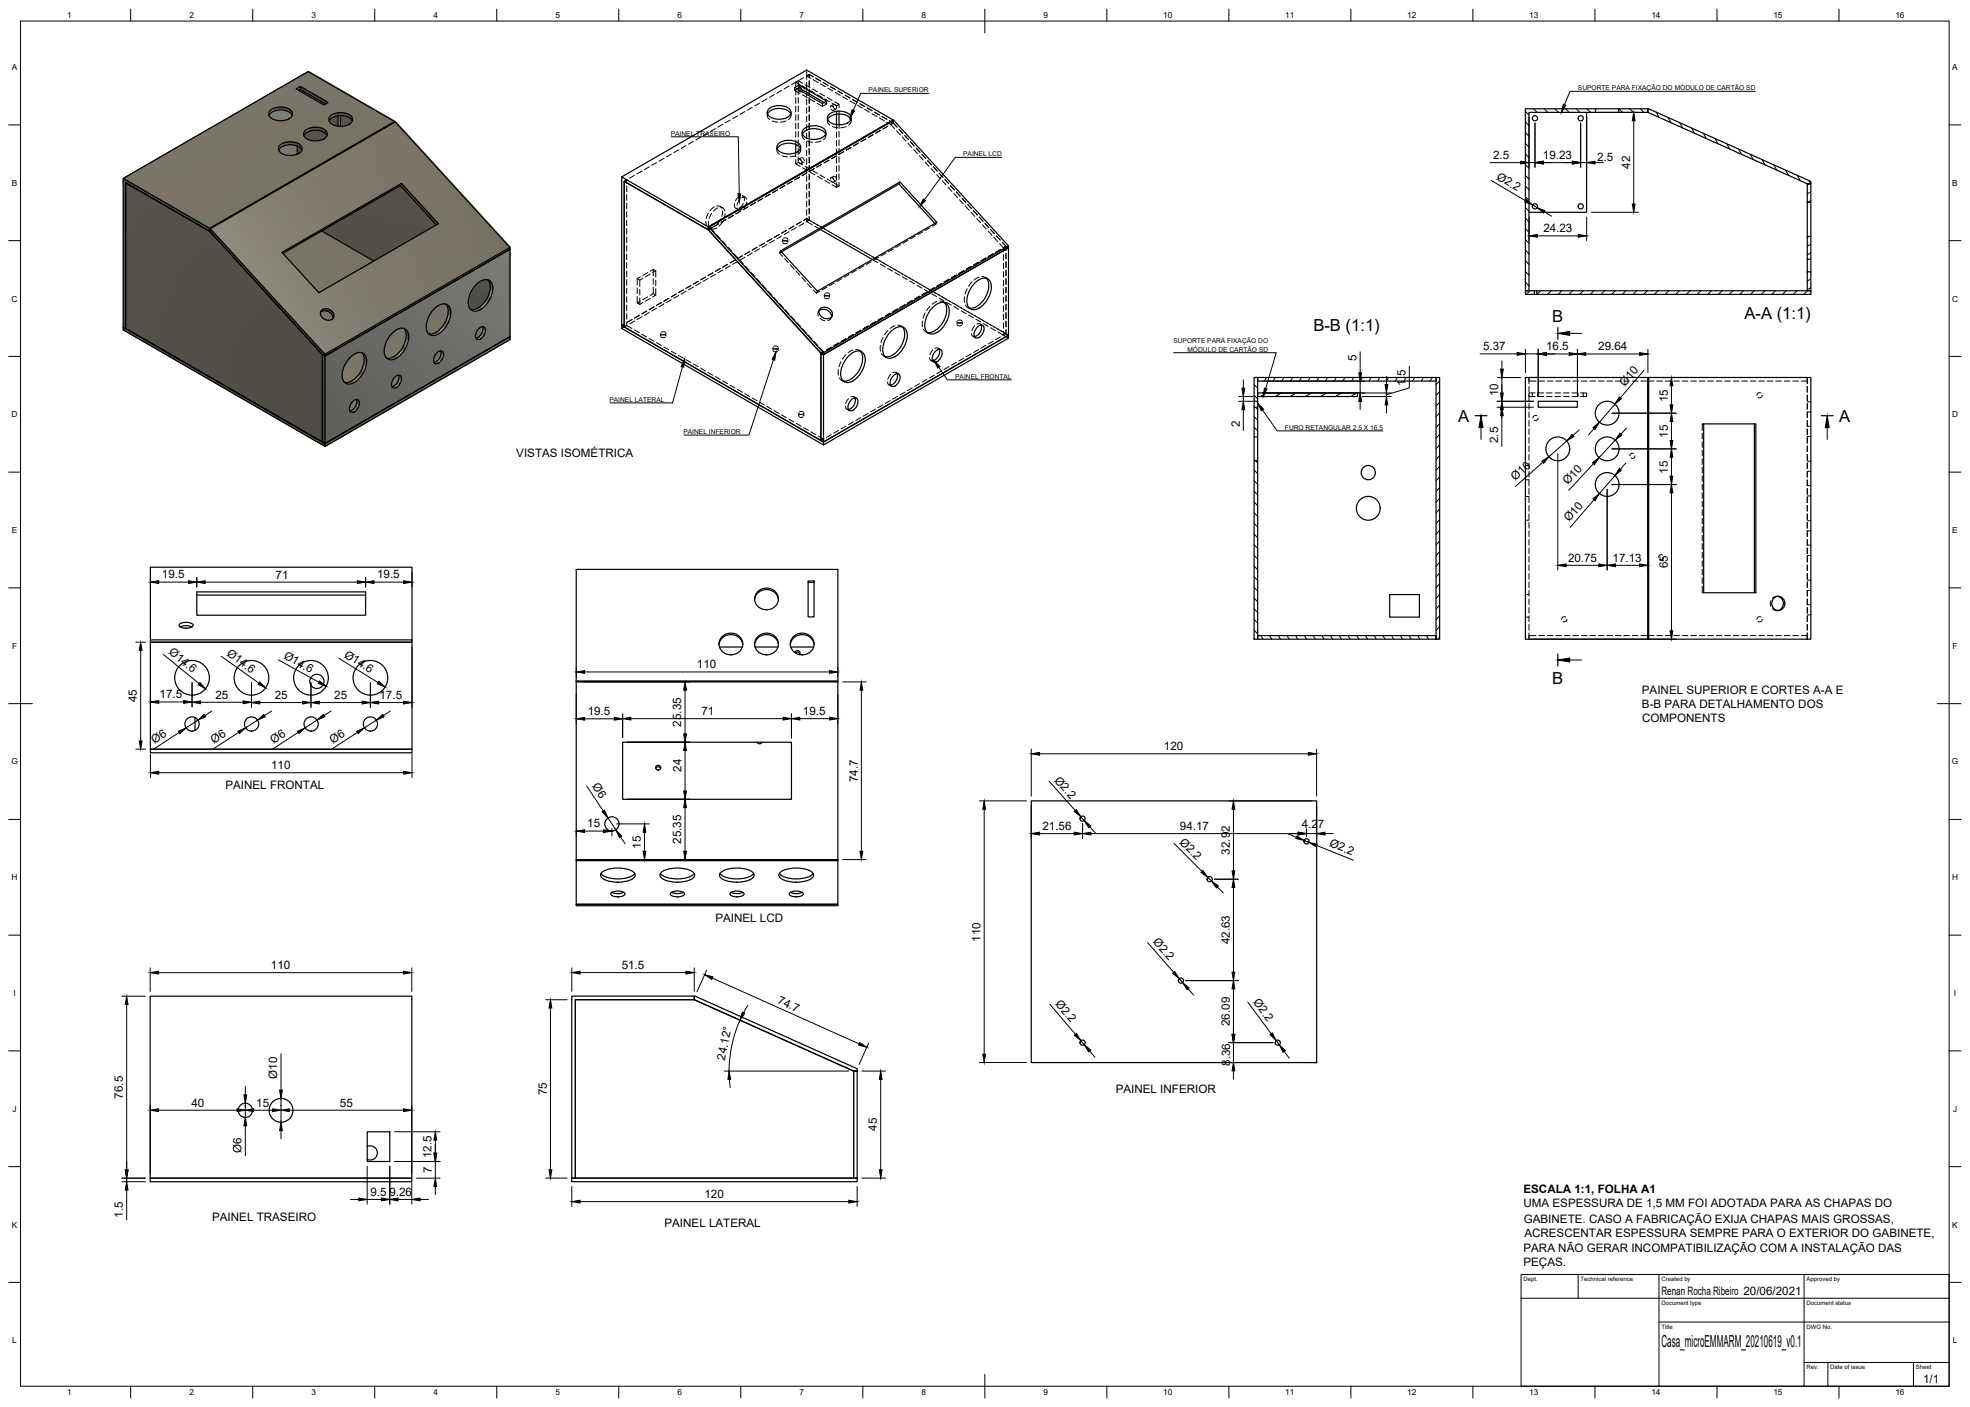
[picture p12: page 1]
VISTAS ISOMÉTRICA; PAINEL FRONTAL; PAINEL SUPERIOR; PAINEL TRASEIRO; PAINEL LATERAL; FURO RETANGULAR 2.5 X 16.5; PAINEL LCD; PAINEL INFERIOR

SUPORTE PARA FIXAÇÃO DO MÓDULO DE CARTÃO SD

SUPORTE PARA FIXAÇÃO DO
MÓDULO DE CARTÃO SD

PAINEL SUPERIOR E CORTES A-A E
B-B PARA DETALHAMENTO DOS
COMPONENTS

ESCALA 1:1, FOLHA A1
UMA ESPESSURA DE 1,5 MM FOI ADOTADA PARA AS CHAPAS DO
GABINETE. CASO A FABRICAÇÃO EXIJA CHAPAS MAIS GROSSAS,
ACRESCENTAR ESPESSURA SEMPRE PARA O EXTERIOR DO GABINETE,
PARA NÃO GERAR INCOMPATIBILIZAÇÃO COM A INSTALAÇÃO DAS
PEÇAS.

Dept. | Technical reference | Created by Renan Rocha Ribeiro 20/06/2021 | Approved by

Document type | Document status

Title Casa_microEMMARM_20210619_v0.1 | DWG No.

Rev. | Date of issue | Sheet 1/1

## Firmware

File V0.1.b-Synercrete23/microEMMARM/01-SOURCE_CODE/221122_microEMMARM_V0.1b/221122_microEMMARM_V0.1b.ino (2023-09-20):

/*
  GENERAL SKECTH INFORMATION:
*/

///////////////////////////////////////////////////////////////////// INCLUDING LIBRARIES /////////////////////////////////////////////////////////////////////

//Libraries for I2C communication, external ADC (ADS1115 module), external RTC (DS3231 module), and I2C LCD
#include <Wire.h>
#include "ADS1X15.h"
#include <uRTCLib.h>
#include <LiquidCrystal_I2C.h>

//Libraries for SD card module
#include "SdFat.h"
#include <SPI.h>

//Library for temperature and humidity sensor (DHT22 module)
#include "DHT.h"


///////////////////////////////////////////////////////////////////// DEFINE GLOBAL VARIABLES /////////////////////////////////////////////////////////////////
//Definition of a structure to hold variables for current state of system configuration
typedef struct
{
  byte samplingFrequencyOption; //sysConfig.samplingFrequencyOption mapping: #1-64Hz/#2-128Hz/#3-250Hz/#4-475Hz/#5-860Hz
  byte samplingDurationOption; //sysConfig.samplingDurationOption mapping: #1-1s/#2-10s/#3-60s/#4-90s/#5-120Hz
  byte sleepDurationOption; //sleedDurationOption mapping: #1-1s/#2-60s/#3-300s/#4-500s/#5-600s
  byte numberOfActiveChannelsOption; //sysConfig.numberOfActiveChannelsOption mapping: #1-1/#2-2/#3-3/#4-4
  byte tempHumSensorOption; //sysConfig.tempHumSensorOption mapping: #1-is On/#2-is off
} systemConfiguration;

//Define default state for system configuration
//The codification of system states is defined in the defintion of the systemConfiguration struct
#define samplingFrequencyOption_Default 5
#define samplingDurationOption_Default 4
#define sleepDurationOption_Default 3
#define numberOfActiveChannelsOption_Default 1
#define tempHumSensorOption_Default 1

//Instantiate the systemConfiguration variable "sysConfig" with default values
systemConfiguration sysConfig = {samplingFrequencyOption_Default,
                                 samplingDurationOption_Default,
                                 sleepDurationOption_Default,
                                 numberOfActiveChannelsOption_Default,
                                 tempHumSensorOption_Default
                                }; //Default configuration

//Pins configuration for interface buttons at top pannel
//#define PAUSE_BUTTON 9
//#define MINUS_BUTTON 8
//#define PLUS_BUTTON 4
//#define ARROW_BUTTON 5
#define PAUSE_BUTTON 1
#define MINUS_BUTTON 8
#define PLUS_BUTTON 4
#define ARROW_BUTTON 0
//Pins configuration for analog I/O pins at front pannel
#define AIO_D1 A0
#define AIO_D2 A1
#define AIO_D3 A2
#define AIO_D4 A3

//Define codification for printing messages on LCD screen
#define WELCOME_SCREEN 7
#define INITIALIZING_SD_SCREEN 6
#define SD_INITIALIZED_SCREEN 28
#define SYSCNFGFILE_NOT_OPEN_SCREEN 38

//ADXL335 accelerometer variables
//There is just one variable because only one channel is monitored each time
uint16_t adsLastValue = 0;

//External ADC (ADS1115 module) definitions
//Instantiation of a ADS1115 object
ADS1115 ads(0x48);
//Configuration of parameters and pis for the ADS1115 module
byte currentChannel = 1;
const byte alertPin = 3;
byte saveInSD = 0; //Parameter that 
//==============
//IMPORTANT INFO:
//      For greater performance, the ADS1115 is used with its hardware interrupt pin.
//      Each time a new sample is ready to be read, the ALRT pin indcates for an ATMega interrupt pin that 
//    a new measurement should be performed. This functionality is called Interrupt Service Routine (ISR).
//      Each time an interrupt occurs, the microprocessor interrupts everything being done and executes a section of code (or function).
//      Because things shouldn't be hanging too long, the function to be executed should be as small as possible and ideally not recursive,
//    at the risk of the ISR beng repeatedly called before being completely run and stay stucked within itself.
//      The function samplingAlert() below is the function performed when ADS1115 raises an ISR flag.
//      It was implemented to be as brief as possible, although it is somewhat recursive: it enables interrupts within itself so I2C communication can occur
//    with the external ADC (ADS1115 module), since I2C communication requires ISR. Tests have never indicated the system to remain stucked within this 
//    function, which indicates it is fast enough for the ISR to work reliably without freezing the system.
//==============
void samplingAlert() {
  //==============
  //IMPORTANT INFO:
  //      The structure of this ISR is based on the discussions made on https://forum.arduino.cc/t/using-i2c-inside-an-interrupt/308125/2. A PDF copy of
  //    this thread can be found on Reference 1 of the source code, in case the Arduino Forum is offline or does not keep the original thread.
  //==============
  static bool IAmRunning = false; //Variable that will allow indicating this ISR function is running.
  //==============
  //IMPORTANT INFO:
  //      IAmRunning is a static local variable. The first time samplingAlert() is run, IAmRunning is initialized, but it is never initialized again
  //    and its value is preserved between different calls of samplingAlert().
  //      Check https://techexplorations.com/guides/arduino/programming/static/ for more info on static variables.
  //==============
  if (IAmRunning) return; //This will finish this run of samplingAlert() if it was called on top of other samplingAlert() already runnin,
                          //so to mitigate recursive calls that could freeze the system. 
  IAmRunning = true; //Indicates the system that a samplingAlert() is being run.
  interrupts(); //Enable interrupts so I2C and communication to external ADS (ADS1115 module) can work.
  adsLastValue = ads.getValue(); //Gets the value from ADS1115. Remember that we are here just because ADS1115 raised an ISR flag saying a new value was ready to be read.
  saveInSD = 1; //Signalizes the system that a new measurement has been read and is ready to be saved to log file
  IAmRunning = false; //Indicates the system that the on-going samplingAlert() has finished. 
}

//Instantiate RTC clock object
uRTCLib rtc(0x68);

//Instantiate LCD object
LiquidCrystal_I2C lcd(0x27, 16, 2); // set the LCD address to 0x27 for a 16 chars and 2 line display

//microSD card module pin and variable definitions
#define chipSelect 2 //CS pin from microSD module
unsigned short logOrdinal[4] = {0, 0, 0, 0}; //Variable to store current ordinal for save files associated to each of 4 measurement channels 
char logFile[10]; //Variable to allow constructing the current file log name.
#define sysConfgFileName "SYSCFG.txt"
//Instantiate a SD object
SdFat32 SD;
//Instantiate a file object
File32 currentOpenFile;
//Variable to store the pre-allocation size used to crease files in the microSD card to speed up the process
uint32_t PREALLOCATE_SIZE  =  0;
//Configurations for the microSD module.
//These configurations were taken directly from ExFatLogger example from SDFat.h library
#define SPI_CLOCK SD_SCK_MHZ(50)
//This structure tries to select the best SD card configuration
#if HAS_SDIO_CLASS
#define SD_CONFIG SdioConfig(FIFO_SDIO)
#elif  ENABLE_DEDICATED_SPI
#define SD_CONFIG SdSpiConfig(SD_CS_PIN, DEDICATED_SPI, SPI_CLOCK)
#else  // HAS_SDIO_CLASS
#define SD_CONFIG SdSpiConfig(SD_CS_PIN, SHARED_SPI, SPI_CLOCK)
#endif  // HAS_SDIO_CLASS

//Temperature and humidity sensor definitions
#define DHTPIN 9 //Data pin for DHT22
#define DHTTYPE DHT22   //DHT 22 (AM2302), AM2321
//Instantiate a DHT object
DHT dht(DHTPIN, DHTTYPE);
//Variable to store the measurements taken from the sensor
float dhtValue = 0;

//Definition of parameters associated to sampling on measurement sessions
//They will be populated during runtime accordingly to the configuration of the system
unsigned short samplingFrequency = 0; //Sampling frequency during a measurement session
unsigned long samplingDuration = 0; //Duration of each measurement session
unsigned long sleepDuration = 0; //Duration of sleep session
unsigned long startTime = 0; //Variable to register the start of each loop (measurement and sleep sessions), so they can be timed

///////////////////////////////////////////////////////////////////// CUSTOM CHARACTERS FOR LCD /////////////////////////////////////////////////////////////////
const byte microSymbol_1[8] = {
  //big μ symbol - first quarter
  B11111,
  B00001,
  B00001,
  B10001,
  B10001,
  B10001,
  B10001,
  B10000
};
const byte microSymbol_2[8] = {
  //big μ symbol - second quarter
  B11111,
  B10000,
  B10000,
  B10001,
  B10001,
  B10001,
  B10001,
  B00001
};
const byte microSymbol_3[8] = {
  //big μ symbol - third quarter
  B10000,
  B10001,
  B10001,
  B10001,
  B10001,
  B00001,
  B00001,
  B11111
};
const byte microSymbol_4[8] = {
  //big μ symbol - fourth quarter
  B00001,
  B11100,
  B11100,
  B11111,
  B11111,
  B11111,
  B11111,
  B11111
};
const byte microSymbol_5[8] = {
  //black block
  B11111,
  B11111,
  B11111,
  B11111,
  B11111,
  B11111,
  B11111,
  B11111
};
const byte microSymbol_6[8] = {
  //in line μ (micro) character
  B00000,
  B11010,
  B01010,
  B01010,
  B01110,
  B01001,
  B01000,
  B00000
};
const byte microSymbol_7[8] = {
  B00000,
  B00100,
  B00110,
  B11111,
  B11111,
  B00110,
  B00100,
  B00000
};
const byte pauseButtom_Symbol[8] {
  B00000,
  B11011,
  B11011,
  B11011,
  B11011,
  B11011,
  B11011,
  B00000
};
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

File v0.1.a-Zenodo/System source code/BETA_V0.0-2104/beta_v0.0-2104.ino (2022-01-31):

/*
  GENERAL SKECTH INFORMATION:
  ACCELEROMETER SENSOR: ADXL335
  SETUP: 
    - NO LCD;
    - NO DHT22 (TO INCLUDE DHT, UNCOMMENT THE READTEMPERATURE LINES;
    - WITH RTC Clock;
  CALIBRATION: MANUAL
*/

///////////////////////////////////////////////////////////////////// INITIAL DECLARATIONS /////////////////////////////////////////////////////////////////////

#include <Wire.h>
#include <SPI.h>
#include <SD.h>
#include <stdlib.h>
#include <Adafruit_ADS1015.h>
#include "DHT.h"
#include <MemoryFree.h>
#include <uRTCLib.h>

//RTC clock object
uRTCLib rtc(0x68);


//Config controls (button and potentiometer
#define PUSH_BUT 6
#define POT_PIN 1
#define RED_PIN 3
#define OTHER_PIN 7
#define OTHER_PIN2 5

//ADC115 definitions
//soligen's library added variables, for continuos mode
const int alertPin = 2; //////////////////////////////////////////////// YOU NEED TO CONNECT THIS FOR CONTINUOS MODE
volatile bool continuousConversionReady = false;
int adcChannel = 1;
Adafruit_ADS1115 ads(0x48); /* Use this for the 16-bit version */
//Adafruit_ADS1015 ads;     /* Use thiS for the 12-bit version */

//ADXL 335 variables
int16_t adcX, adcY, adcZ;

//Instantiate LCD object
//LiquidCrystal_I2C lcd(0x3F, 2, 1, 0, 4, 5, 6, 7, 3, POSITIVE);

//SD card pin
const int CS = 4;
#define chipSelect 4 //SD card pin
int logIteration = 1; //Variable to allow creation of multiple files in the same voidloop (logfile1.txt, logfile2.txt, etc)
char logFile[16];

//Sampling parameters
int samplingFrequency = 0; //Em Hz. It will be set in void setup().
unsigned long iniTime = 0;
unsigned long endTime = 0;
unsigned long samplingDuration = 0; //Sampling duration in seconds.
unsigned long samplingStartTime = 0; //Variable to know when sampling started, to allow for sampling stop.

//Real experimental setup parameters (EMM-ARM - added on 29/05/2018)
#define sleepDuration 300000 //Sleep or 5 minutes (in milliseconds), after each sampling burst
unsigned long sleepTime = 0; //Will account the time the system started to sleep, to allow counting the 10 minutes sleep

//Calibration parameters
//int mean_ax, mean_ay, mean_az, mean_gx, mean_gy, mean_gz, state = 0;
//int ax_offset, ay_offset, az_offset, gx_offset, gy_offset, gz_offset;
//#define buffersize 1000   //Amount of readings used to average, make it higher to get more precision but sketch will be slower  (default:1000)
//#define acel_deadzone 8   //Acelerometer error allowed, make it lower to get more precision, but sketch may not converge  (default:8)
//#define giro_deadzone 1   //Giro error allowed, make it lower to get more precision, but sketch may not converge  (default:1)

//Error parameters: count how many errors have occurred in the sketch, separated by type.
int SDInitError = 0; //Error related to system unable to perform SD.begin method succesfully.
int accelInitError = 0;  //Error related to system unable to perform accelgyro.testConnection() method succesfully.
int SDFileError = 0; //Error related to system unable to open SD file succesfully.

////DHT 22 Declarations
#define DHTPIN 8    // what digital pin we're connected to
#define DHTTYPE DHT22   // DHT 22  (AM2302), AM2321
DHT dht(DHTPIN, DHTTYPE);
float t = 0;

//Motor pin for concrete version excitation
byte motorPin = 9;
byte motorValue = 255;
byte delayTime = 500;

///////////////////////////////////////////////////////////////////// SETUP /////////////////////////////////////////////////////////////////////
void setup() {

  //---------------------------------------------------------------------------------------------------------------------------------------------
  //GENERAL DECLARATIONS
  //---------------------------------------------------------------------------------------------------------------------------------------------
  pinMode(PUSH_BUT, INPUT); //Configure button
  pinMode(RED_PIN, OUTPUT); //Configure led pin
  pinMode(OTHER_PIN, OUTPUT); //Configure led pin
  pinMode(OTHER_PIN2, OUTPUT); //Configure led pin
  pinMode(motorPin, OUTPUT); //Motor pin for excitation in concrete version
  //Initiate LCD
  //lcd.begin (16, 2);
  //lcd.setBacklight(HIGH);
  //No sense in checking LCD connection... There will be nothing to print the error on!
  //writeLCD("Iniciando", "Aguarde", 0);
  blinkLED(RED_PIN, 500, 4);
  blinkLED(OTHER_PIN, 500, 4);

  //--------------------------------------------------------------------------------------------
  // ADS1115 CONFIGURATION
  //--------------------------------------------------------------------------------------------

  // The ADC input range (or gain) can be changed via the following
  // functions, but be careful never to exceed VDD +0.3V max, or to
  // exceed the upper and lower limits if you adjust the input range!
  // Setting these values incorrectly may destroy your ADC!
  //                                                                ADS1015  ADS1115
  //                                                                -------  -------
  // ads.setGain(GAIN_TWOTHIRDS);  // 2/3x gain +/- 6.144V  1 bit = 3mV      0.1875mV (default)
  ads.setGain(GAIN_ONE);           // 1x gain   +/- 4.096V  1 bit = 2mV      0.125mV
  // ads.setGain(GAIN_TWO);        // 2x gain   +/- 2.048V  1 bit = 1mV      0.0625mV
  // ads.setGain(GAIN_FOUR);       // 4x gain   +/- 1.024V  1 bit = 0.5mV    0.03125mV
  // ads.setGain(GAIN_EIGHT);      // 8x gain   +/- 0.512V  1 bit = 0.25mV   0.015625mV
  // ads.setGain(GAIN_SIXTEEN);    // 16x gain  +/- 0.256V  1 bit = 0.125mV  0.0078125mV
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

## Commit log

2021-04-21 Add files via upload
    This is the Fritzing file of the electronic schematic version of the microEMMARM v0.0, as shown on the Figure 3 of the research paper "Low-cost system for early age E-modulus monitoring of cement-bas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
    [20210421_SCHEMATICS.fzz]
2021-04-21 Add files via upload
    This is the microEMMARM v0.0 version.
    This is a bare-minimum version of the system, as equivalent to the Figure 3 of the research paper "Low-cost system for early age E-modulus monitoring of cement-based materials".
    [20210421_microEMMARM_v00.fzz]
2021-04-21 Add files via upload
    This is the schematic for the microEMMARM v0.1.
    This version is the bare-minimum v0.0 version, with expanded ADC channels and digital channels for controlling external devices (e.g. motors for artificial excitation). The version is still under tes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
    [20210321_SCHEMATICS_v01.fzz]
2021-04-22 Add files via upload
    This is the Arduino source code file for the v0.1 system.
    The source code may be readily uploaded to any Arduino ou ATMega microprocessor through the Arduino IDE.
    This version supports one read channel of the ADC and one digital channel for controlling external devices.
    Expansion to more channels, as allowed by the v0.1 schematic, is simple, but a forthcoming version may already incorporate that.
    In its original form, the source code does not measure the temperature and humidity. In order to incorporate that, the user needs to uncomment the "dht.readTemperature();" and subsequent lines.
2022-01-09 Delete 20210321_SCHEMATICS_v01.fzz
    This file was deleted because it contained route tracing errors that, although did not affect the functioning of the system, hindered its constructability and some of its functioning (namely ADS1115 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
    [20210321_SCHEMATICS_v01.fzz]
2022-01-09 Delete 20210421_microEMMARM_v00.fzz
    Deleting 20210421_microEMMARM_v00.fzz because it contained minor mistakes (e.g., unnecessary pull-down resistors and lack of ALRT pin connection for ADS1115). A revised version will be added.
    [20210421_microEMMARM_v00.fzz]
2022-01-31 Corrected v0.0 version, minor changes
    Correction of resistors added to SD Card Module lines were corrected (i.e., they were removed as are not required), removal of unnecessary RC filter close to ADC lines.
    [2201_v0.0.fzz]
2022-01-31 Standardization and organization
    Organization and standardization of files. All file names were standardized. Schematics and breadboard images were generated for beta_v0.0 system version. Source code was renamed.
    [2201_v0.0.fzz, beta_v0.0-2201.fzz]
2022-12-01 Organization repository to archive Zenodo releases
    [20221118_SCHEMATICS-COMPLETE.fzz, BOM_COSTS.xlsx, beta_v0.0-2201.fzz]
2023-12-30 Release of version v.0.2
    [0-BACK-PANEL-toPrint v1.stl, 0-BOTTOM-PANEL-toPrint v1.stl, 0-FRONT_PANEL-toPrint v1.stl, 0-SIDE-PANEL-1-toPrint v1.stl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]
